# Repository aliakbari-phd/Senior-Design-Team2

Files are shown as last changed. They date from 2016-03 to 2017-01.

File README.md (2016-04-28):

# Wearable Computers for Quantification of Lower Back Disorders
## Team 7: Ben Johnston, Kevin Burns, Alex Dubois, Benny Chan

## Abstract:

Using a combination of wearable inertial sensors and a Microsoft Kinect, our group will create a cost effective system to model the motion of a patient’s lower back in order to quantify the severity of lumbar spinal disorders. This will provide an objective pre-surgical screening, where current methods are largely subjective.

Two small wearable inertial sensors will be placed in line with the patient’s T12 and L5 vertebrae to model integral points on the patient’s back. The patient will be asked to perform simple back exercises to thoroughly evaluate the range of lumbar motion in all planes. The Kinect, a relatively inexpensive motion capturing camera, will be introduced to monitor the patient’s posture and assist the wearable sensors with an all-encompassing look at the subject.

This system would be used in a physician’s clinic room and relatively simple to set up. There are other, more accurate, motion capture systems available that use infrared emission and detection to isolate specific markers on a subject. However, these options consume a large amount of space and cost hundreds of thousands of dollars or more.

## Introduction:

Lower back disorders (LBDs) are the most common work-related musculoskeletal disorders. This translates to a significant cost to society. However, in 80 to 90 percent of cases, precise diagnosis is not known for disabling LBDs. An objective, quantified measure of the severity of lower back disorders is needed. A proven metric can provide a benchmark for returning to the job without risk of exacerbating the disorder, as well as a delineation between normal variability of pain and a disorder.

Our goal is to create a system that can monitor the movement of the patient’s lower back during a specified exercise to characterize and quantify the severity of a lower back disorder. The exercise requires the patient to stand up straight with their arms crossed over one another with their hands resting on their chest. The patient then bends straight down, with their hands remaining on their chest, and returns to the original position. This exercise is repeated as many times as the patient can without undue pain in a 15 second window. This exercise is repeated at 15 degrees, 30 degrees, and as far as the patient can rotate in either direction from the sagittal plane. Repeated motion testing has varied results and can thus be used to provide a full characterization of a human process. 

Our team will combine the use of wearable inertial sensors and a Microsoft Kinect working in tandem to track this motion. The inertial sensors will deliver the pertinent angular characterization of the lower back, and the Kinect will assist in error correction of the inertial sensors as well as ensure proper patient posture throughout the exercise. This data will be synchronized and corrected for standard sensor error. The corrected data will be analyzed to provide the severity quantification as well as being stored on a database. The motion and quantified information will be shown on a graphical user interface on the operator’s computer and posture correction feedback will be shown on a separate display monitor.

## Block Diagram:

Block Diagram

## Concept Sketch:

Concept Sketch

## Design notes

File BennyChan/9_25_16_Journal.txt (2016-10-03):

1. Fixed calculation of flex angle to reflect joint between spineMid and spineBase instead of spineShoulder.
Justification: This is because the location of one of the IMU is located right below the chest, which the SpineMid is closer to compared with the SpineShoulder.
2. Cleaned IMU data from the kinect integration
Justification: The IMU showed unecessary amount of noise, which a low-pass filter of 1K was applied

Tasks:
Test the database of gesture detector to provide more reliable feedback 
Modify GUI as required for patient ease

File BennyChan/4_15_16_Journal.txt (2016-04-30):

Updated Integrated Sensor Code to start implementing data structures

Tasks:
Finish updating integrated sensor code
Create a basic database
Create a basic GUI

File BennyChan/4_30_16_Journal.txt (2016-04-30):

Fixed sagittal angle, computed flex angle and modified GUI to include feedback for angles.

Tasks:
Provide in-depth flowchart
Modify GUI as required

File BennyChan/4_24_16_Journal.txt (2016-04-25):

Created Display Feedback Database, as well as, the GUI for the patient displaying a set of gestures that patient has to do during test.

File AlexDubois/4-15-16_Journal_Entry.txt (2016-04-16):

Updated Integrated Sensor Code to start implementing data structures

Tasks:
Finish updating integrated sensor code
Create a basic database
Create a basic GUI
Find out how to do basic data analysis to find quantified level of LBD

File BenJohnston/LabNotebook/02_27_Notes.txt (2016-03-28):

Sensors are finally online and linked to the computer through Bluetooth with some fancy C# code.

Attended the Design Blitz from 10AM to noon.

Obtained more information on the MotionNet sensor. The actual sensor module is a MPU9150. Datasheet: https://dlnmh9ip6v2uc.cloudfront.net/datasheets/Sensors/IMU/PS-MPU-9150A.pdf

The bluetooth module of the MotionNet Sensor is the BC127, which is bluetooth 4.0. Datasheet: https://developer.mbed.org/media/uploads/bckln/datasheet-bc127.pdf

The batteries used are 400 mAh, 3.7 small batteries. One of them has already died, further reinforcing the aim to rework the power system of the sensors a bit.

I made good progress on the ICD Document. I created the outline and finished my sections of the outline. I redid the formatting of the document template and started to work on my sections.

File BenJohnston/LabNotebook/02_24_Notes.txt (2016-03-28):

We have collected the MotionNet Sensors, a combination of accelerometers, gyroscopes, and magnetometers connected to a bluetooth output on a small PCB, made at UTDallas by Lu Sun Zhongjun, February 2015. We obtained 3 from Jian Wu and a mini-USB cord to hook up the computer.

Jian recommends Visual Studio, as the code for the sensors is written in C#, a graphical version of C. Jian is also sending instructions on how to set them up, some basics physics of how they work, and some other useful info.

These will be the focus of my part of the project, specifically combatting the drift they create.

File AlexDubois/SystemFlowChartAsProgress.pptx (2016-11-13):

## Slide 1

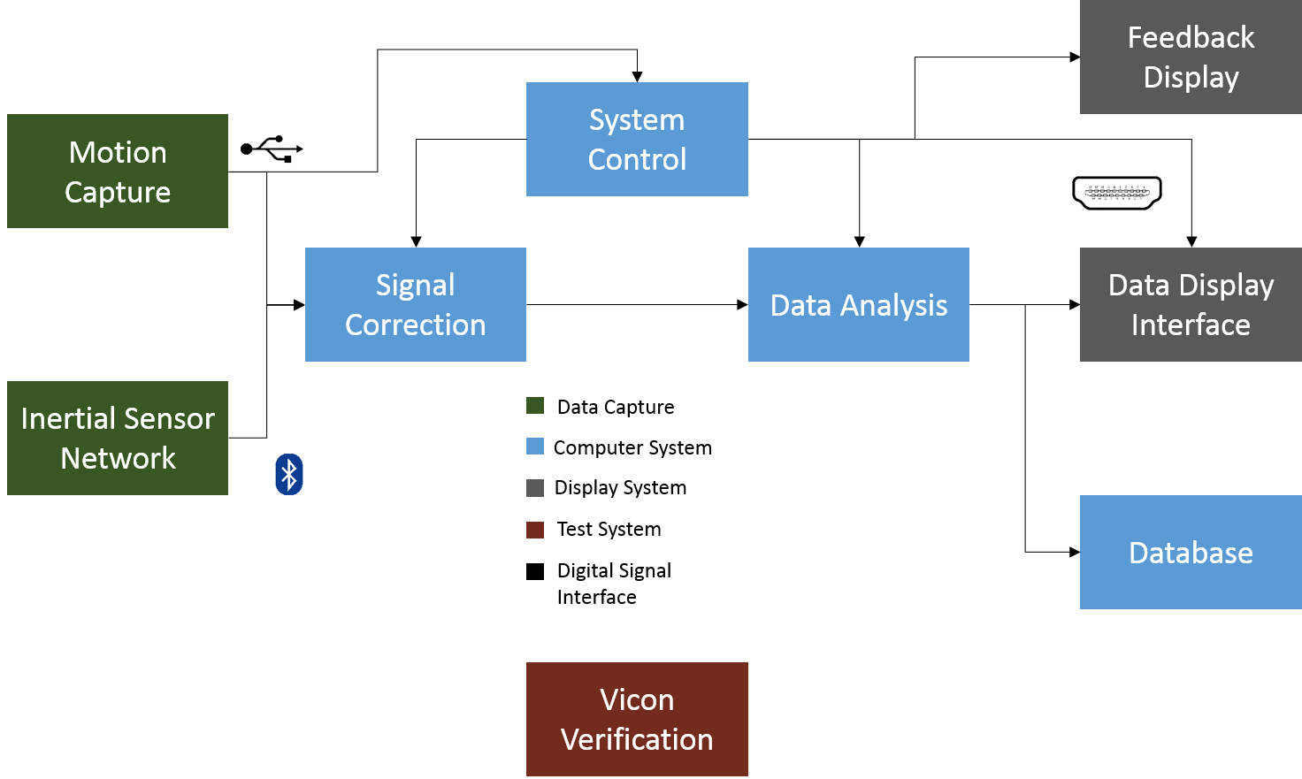
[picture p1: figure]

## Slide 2

Feedback Display

System Control

Motion Capture

Data Display Interface

Inertial Sensor Network

Integrated

Signal Correction

Data Analysis

Database

Requires integration refinement

Not yet integrated

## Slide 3

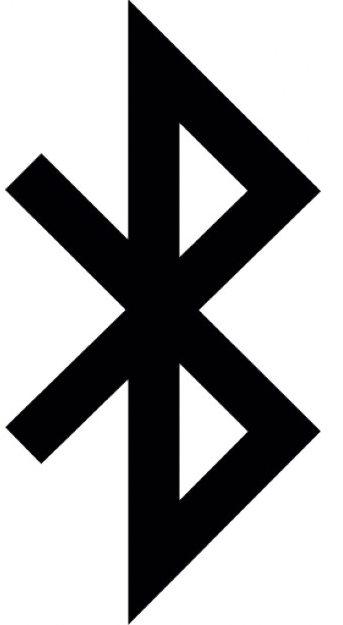
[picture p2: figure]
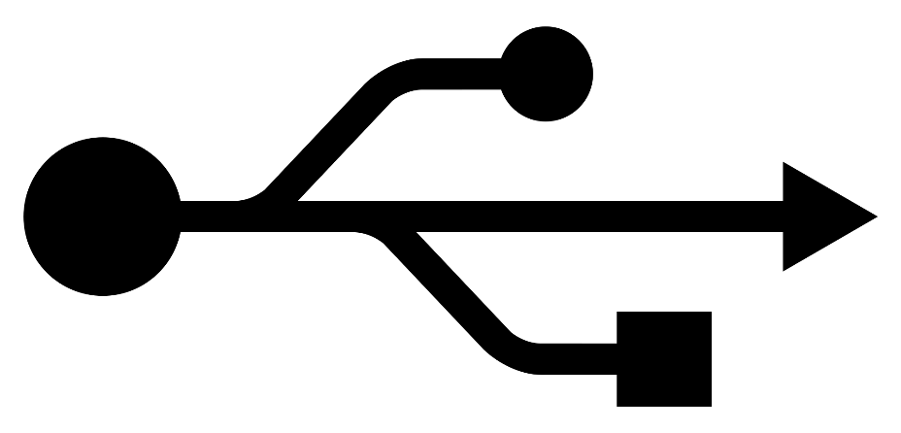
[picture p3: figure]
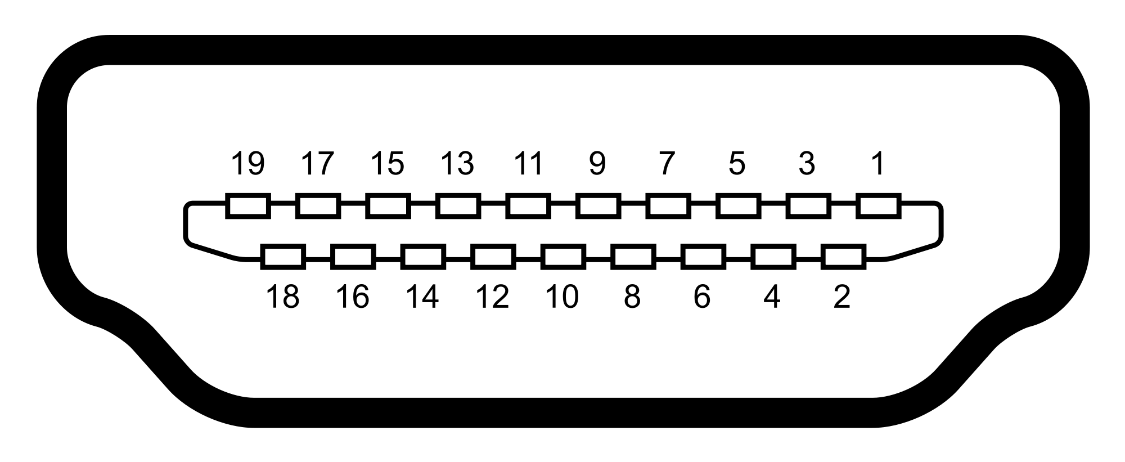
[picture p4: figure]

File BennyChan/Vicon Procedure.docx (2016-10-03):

- Data management to create database
- Select all vicon cameras
  - Window
    - Camera mode
  - If camera doesn’t come up
    - Right click and reboot
- Mask cameras (takes empty points and ignore them)
  - Click mask
  - Whenever they get blue, stop mask
- Aim camera start
- Calibrate
  - Get wand and place it in the origin
  - Calibration, full calibration
  - Selected cameras
  - 2000
  - 750
  - Auto stop check
  - Press start and move wand to calibrate
  - It will auto stop
  - <0.3 is good in image, <0.1 is better
  - Set wand in origin again
- Set volume origin
  - Press start and set origin
- System tab
  - Core processor
    - Reconstruct
- Subject tab
  - Click 2nd icon
    - Click on ben subject model
- Tools tab and go to the little person and select ben.
  - Start subject capture
  - Pipeline
    - Reconstruct
      - Label
        - Esc
    - File I/O
      - Export ascii delimited
- Save and go live

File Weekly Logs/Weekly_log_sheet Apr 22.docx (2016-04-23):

DATE: Apr 22 2016

INDIVIDUAL PROGRESS

Member Name | Accomplishments | Next Week’s Goal | TA Comments
Kevin Burns | C# Sync code completed C# Signal Correction framework finished C# libraries installed and operational | Complete Signal Correction math operations Operational 3D moving line program completed
Benny Chan | Gesture database generated for feedback display Calculation of angle with respect to Kinect GUI for feedback display | Finish gesture database Analyze angle of Kinect
Alex Dubois | Assisted with: Gesture database Kinect Angle | Database for patient information
Ben Johnston | Quaternian forms of signals achieved correctly Swing testing determined variable velocity drift STEP files for enclosure obtained | Use Quaternian form for manipulation Further swing testing performed for long-term drift Build enclosure in SolidWorks

DATE: Apr 22 2016

PROJECT STATUS SUMMARY

MAIN ACCOMPLISHMENTS

- Method for establishing frame from wearable sensors found
- Quaternian representation of signals achieved
- Gestures for pass/fail of exercises with Kinect Gesture Builder built

MAIN PROBLEMS/ISSUES

- Syncing sensor frame with Kinect frame
- What to do with Quaternian representation of signals
- Kinect tracking during rotated trunk exercises

TEAM DYNAMICS

Answer Y or N to each question

- Are all members on schedule with their respective tasks? Yes_
- Are all members contributing equally to the efforts of the team? _Yes_
- If any member is behind schedule, has this occurred consecutively more than one week? _No_
- Would you like to schedule a meeting with any of the TAs to address issues related to team dynamics? _No_

Weekly Log Sheet

ECEN 403 LAB TEAM: 07

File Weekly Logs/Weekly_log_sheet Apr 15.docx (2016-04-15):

DATE: Apr 15 2016

INDIVIDUAL PROGRESS

Member Name | Accomplishments | Next Week’s Goal | TA Comments
Kevin Burns | C# libraries for graphical interface researched C# libraries for mathematical operations downloaded C# software outline completed Proposal completion | Integrate all downloaded libraries to C# Build framework for visualization portion Finish C# program for Synchronization Metronome sensor testing
Benny Chan | Computation of 3d Join position overtime Proposal completion | Resolve frame difference issue between Vicon and Kinect Gesture control
Alex Dubois | Database datastructure framework initialized Quantification measurements researched Proposal completion | Gesture control Finalize quantification measures
Ben Johnston | Altium license accessed and installed and explored Quaternian conversion of motion data Metronome ordered for sensor testing Proposal completion | 3D printed case file exported from Altium Establish frame to work Kinect Metronome sensor testing

DATE: Apr 15 2016

PROJECT STATUS SUMMARY

MAIN ACCOMPLISHMENTS

- Vicon working and data extracted for comparisons to sensors and Kinect for characterization
- Kinect and sensor integrated code for data collection over time
- Shell codes signal processing and data analysis completed

MAIN PROBLEMS/ISSUES

- Reference framing between Kinect and Vicon, as well as well as sensors and Kinect
- Quantification measures need to be researched more and finalized
- More C# code completion

TEAM DYNAMICS

Answer Y or N to each question

- Are all members on schedule with their respective tasks? Yes_
- Are all members contributing equally to the efforts of the team? _Yes_
- If any member is behind schedule, has this occurred consecutively more than one week? _No_
- Would you like to schedule a meeting with any of the TAs to address issues related to team dynamics? _No_

Weekly Log Sheet

ECEN 403 LAB TEAM: 07

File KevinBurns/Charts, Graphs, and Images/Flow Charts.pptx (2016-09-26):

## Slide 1

System Control Subsystem

System Startup Error Handling

IMU Error Handling

Kinect Error Handling

Control Instructions

Feedback Display Instructions

Data Handling Instructions

If: No error

Display No Error

If: Posture Failure

Display Error to Tech

No “Fail”
Flag Detected

“Fail” Flag
Detected

If: System Error

Display Error to Tech

Pass Data to Quantification

Delete Data and Restart Trial

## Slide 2

Signal Syncing Subsystem

Access Sensor Data

Correct Signal Timing Discrepancies

Sensor Data Bank

In MATLAB, needs to convert to C#

No

All Discrepancies Corrected?

Convert Kinect Data from Position to Angular Velocity

Signal Sync Algorithm

Apply Sync Factor and Store Data

Yes

In C#, ready for integration

Drift Correction

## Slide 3

Drift Correction Subsystem

Access Synced IMU Sensor 1 Data

Signal Syncing

Drift Correction Factor

Access Calibration Data

Drift Correction Algorithm

Determine Drift Factor

Repeat for IMU Sensor 2

Apply Drift Correction to Data

Store Data for Use in Quantification

Quantification

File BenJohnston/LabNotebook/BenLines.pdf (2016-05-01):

- Intro(4+4+4+7+6+4)=29 seconds
- We’re Team 7, Wearable Computers for the Quantification of Lower Back Disorders
- We are mentored by Dr. Jafari of ESP Lab at Texas A&M University
- We’re using wearable inertial sensors combined with a Microsoft Kinect to gather data to model a patient’slower back, and then transmit that data to a central computer.
- These signalswill be synchronized, corrected, and analyzed, giving a quantification of the severity of the patient’s lower back disorder.
- This information will be stored in a database and displayed for a medical technician.
- Wearables(7+6+8+7+6+7)=41 seconds
- Two MotionNet sensors, provided by ESP Lab, will be placed along the lumbar region of the patient’s spine, secured and buttoned to Polar Soft Straps.
- I have collected over 20 hours of tests from the sensors in an attempt to characterize the “drift” error of the IMU’s gyroscopes.
- “Drift” error compounds, reducing the accuracy of the sensors over a long period of time as seen from the raw data on the left. On the right is the correction I have developed thus far.
- Current drift correction models are not viable for hour plus long intervals. Which is the goal for repeated testing without recharging the sensors.
- I will use the accelerometers and Kinect to error check and further the accuracy of the gyroscopes through Kalman filters.
- Additionally, there is a small amount of movement between the PCB and the existing 3D box case, so I am working to print a new, fitted enclosure.
- Vicon (8+5+8)=21 seconds
- We will use a Vicon, a highly accurate motion capture system of infrared cameras focused on a central point, to verify the accuracy of the IMU’s and Kinect.
- Ben Johnston is seen here demonstrating the trunk flex exercise, along with the resultant camera view of the Vicon.
- TheIMU’s, Kinect, and Vicon data must be interpolated into the same relative global frame for the verification. This will be accomplished in the coming months.

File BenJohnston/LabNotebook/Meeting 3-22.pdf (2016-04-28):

# Sensor Presentation

3/22

15 seconds, velocity and best fit line

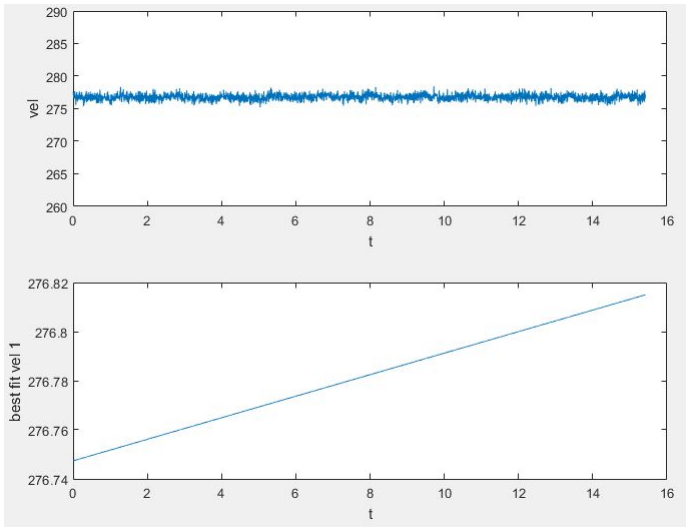
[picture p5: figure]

30 seconds velocity and best fit line

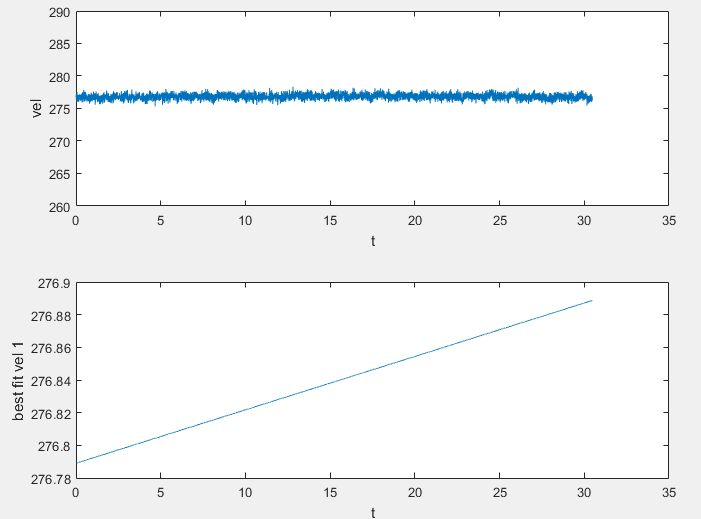
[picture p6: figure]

60 seconds velocity and best fit line

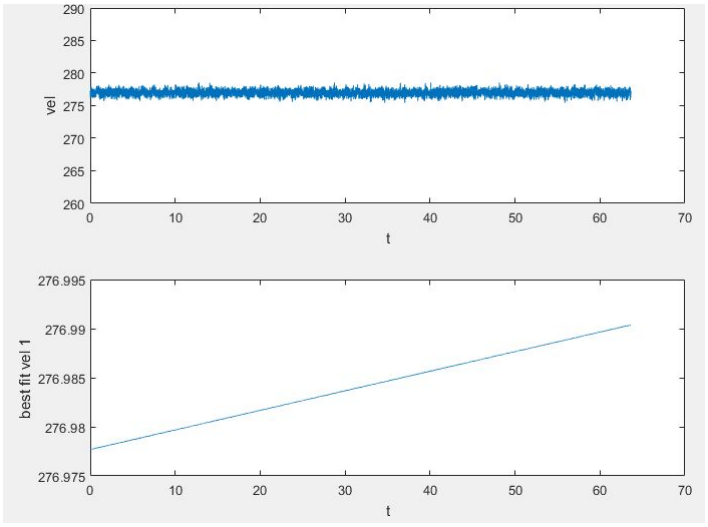
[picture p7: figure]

5 min velocity and best fit line

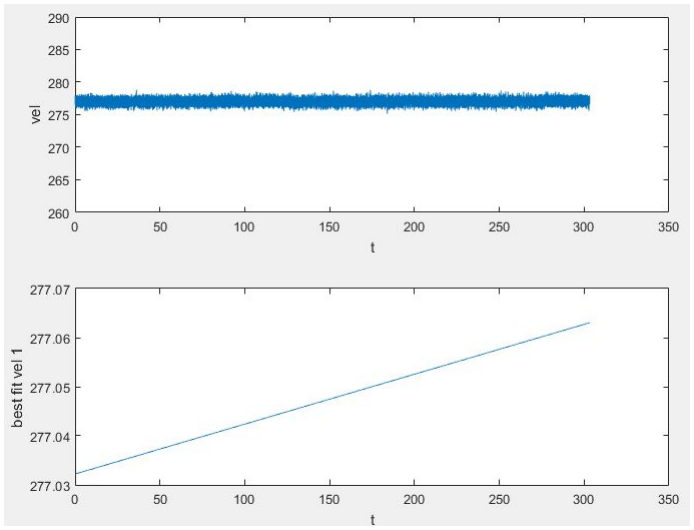
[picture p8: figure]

15 sec, 30 sec, 1 min, 5 min velocities over time

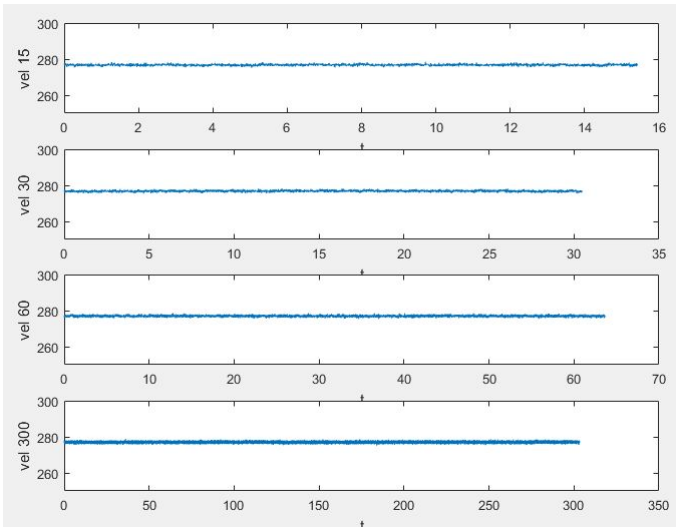
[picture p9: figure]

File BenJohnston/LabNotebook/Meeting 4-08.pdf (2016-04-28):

# Wearable Sensor Testing Report 4/8/2016

All of the following results are from older data with the wearables configured to capture at 200 Hz. When the sensors were changed to 500 Hz, the actual capture rate was inconsistent and the data suffered as a result and was thus unusable. This is what I was trying to convey in an admittedly confusing manner before. I've run many tests but I will highlight a few that I believe to be important. All of the following tests were using the same sensor. Results vary slightly with the sensor, but I wished the following data to be consistent.
Note: All following velocities and distances are found in the Z-axis of the gyroscope.

## LP Player Test

- The following test involves an inertial sensor placed on a rotating LP player.
- Player rotating at 45 rpm (270 degrees per second).
- Test run for 63.02 seconds

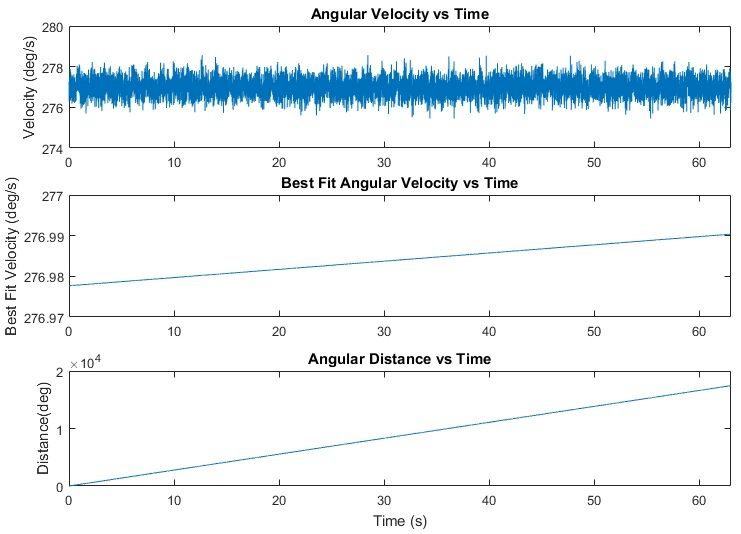
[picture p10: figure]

- Mean Velocity: 276.98 | deg/s | Expected: 270 deg/s
- Final Distance: 17455 deg | | Expected: 17014.4 deg
It is difficult to know how much of the discrepancy between actual and expected is due to inaccuracy in the “45 rpm” setting of the LP player and due to the drift.

## Stationary Test (Power Unplugged vs Plugged)

- Test consists of sensor sitting stationary on undisturbed surface.
- Test run for 7199.2 sec (~2 hours).
- Sensor fully charged and then unplugged.

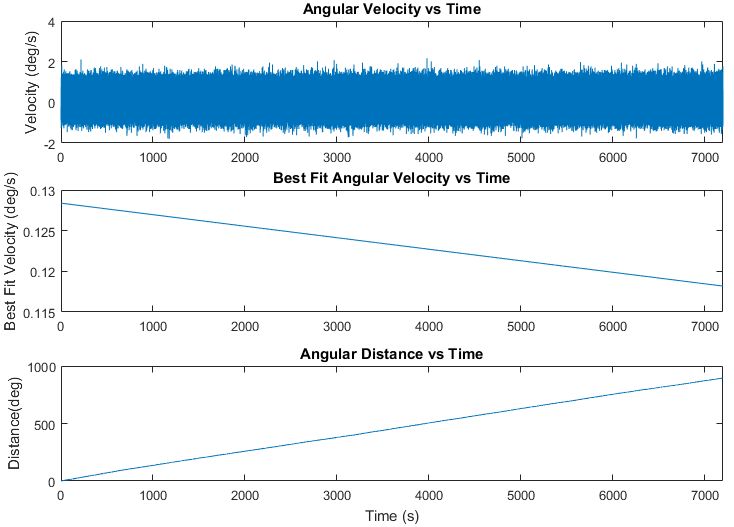
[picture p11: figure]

- Mean Velocity: | 0.123 deg/s | Expected: 0
- Final Distance: | 895.14 deg | Expected: 0
- Corrected Distance: 858.44 deg
- Drift: | 0.0102 deg
“Drift” refers to the difference in starting velocity from the best linear fit line and the ending best fit ending velocity.
Velocity is corrected by subtracting the discrepancy in initial best fit velocity from current best fit velocity from it. Or more simply put, flattening out the best fit line and adjust velocity by the
same amount.
This correction fixes the data by only 4.2%. I believe the main problem to be the inherent offset that the gyroscopes are reading. Even when noise is filtered with a digital low pass filter, there is a clear average offset of ~0.13 degrees per second. This number is different for each sensor. Drift is certainly a function of the voltage of the battery, as shown in the test below with the power cord plugged in for the duration.

- Test is run with sensor sitting stationary on undisturbed surface.
- Sensor fully charged, and plugged into power cord for the duration of test.
- Test run for 7197.9 sec (~2 hours)

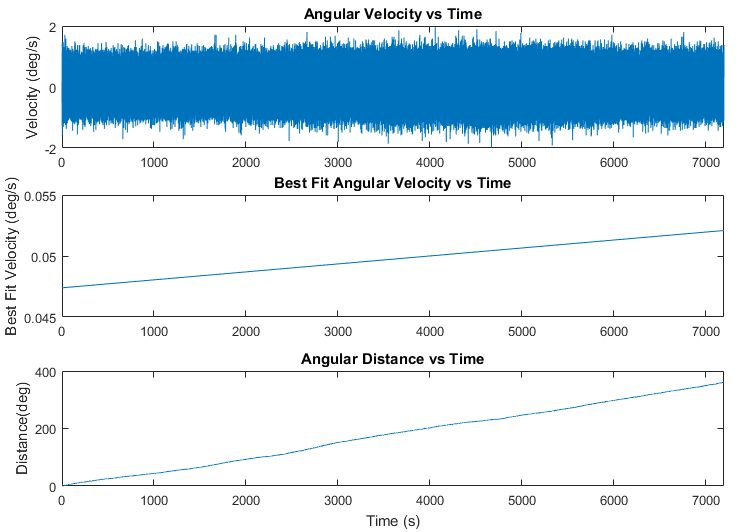
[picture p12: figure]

- Mean Velocity: | 0.0497 deg/s | Expected: 0
- Distance: | 360.75 deg | Expected: 0
- Corrected Distance: 343.84 deg
- Drift: | 0.0047 deg
These results are nearly 2.5 times better than where a sensor is not plugged in. I believe that it would be worth looking into a battery that would more consistently deliver voltage for a longer period of time. This must be taken into account when 3D printing an enclosure for the sensor.

Thank you for your time Dr. Jafari. Please let me know if you have any further questions about my results thus far.

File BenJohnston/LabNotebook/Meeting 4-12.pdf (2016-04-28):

# Inertial Wearable Sensors Presentation

4/12/2016

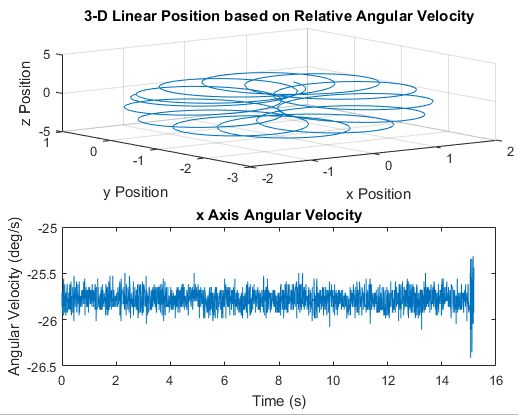
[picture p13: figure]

Test Parameters
- Sensor placed on rotating LP player (rotates in z-axis).
- Duration: 15.18 s
- Capture Rate: 203.1 Hz

Results:
- Actual Z Distance: 4203 deg
- Expected Distance: 4099 deg
- Actual Z Velocity: 277 deg/s
- Expected Velocity: 270 deg/s

Raw Data
- Linear position found based on relative angular velocity.
- Position units are multiplied by radius to find actual position.

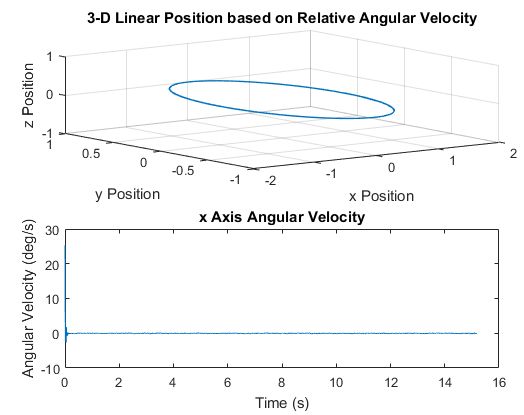
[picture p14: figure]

With Correction

- Angular velocity low pass filtered for noise
- Average velocity recorded while sensor stationary,
treated as constant offset
- Offset subtracted velocity recorded in motion

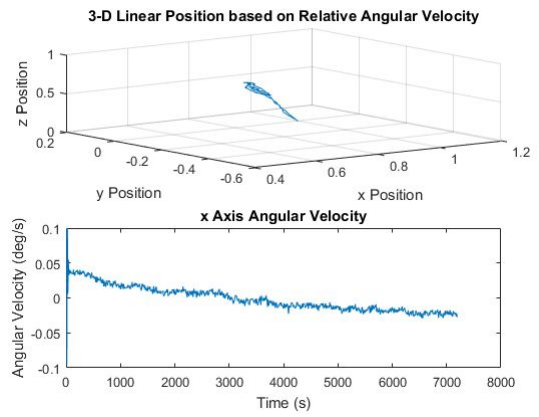
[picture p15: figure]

Test Parameters:
- Sensor stationary on
undisturbed surface.
- Duration: 7199.2 sec (~2hr)
- Capture Rate: 203.0 Hz

Results:
- Voltage Drift (Defined as the difference in starting
angular velocity subtracted by end angular velocity):
0.0597 degrees
- Slope of Drift:
8.293*10^-6 deg/s

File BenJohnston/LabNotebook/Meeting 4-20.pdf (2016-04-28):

# Inertial Sensor Presentation

4/20

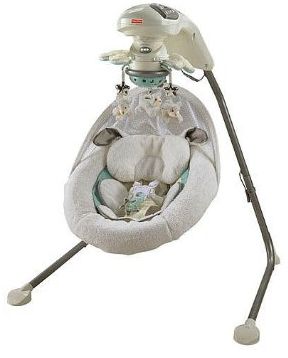
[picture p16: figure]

Fisher Price Platinum Edition Cradle n’ Swing

- Metronome alternative.
- Only suitable metronome: expensive and 3 weeks to ship
- Not perfectly stable in off axes
- Takes time to speed up
- Exact speeds, measurements not known
- Test: Is the ending position same as starting position?

Stationary Testing for Offset Velocity

- Sensor: 01623D
- Test: sensor placed on undisturbed surface for 60 seconds.

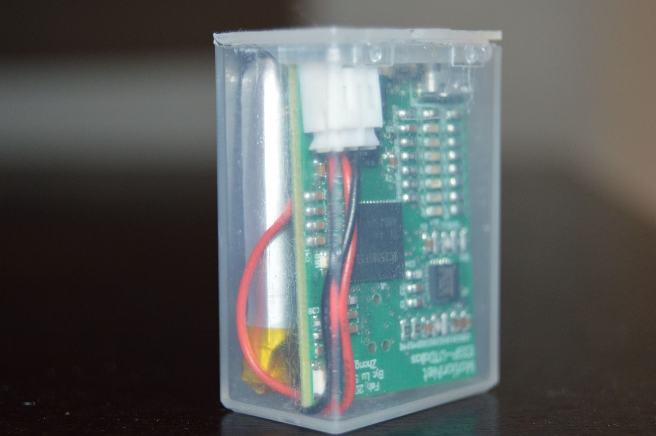
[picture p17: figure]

- Velocity is low pass filtered for noise
- Average velocities in x,y,z are treated as constant offsets
- Mean_x: | -1.2012 deg/s
- Mean_y: | -0.7176 deg/s
- Mean_z: | 0.8495 deg/s

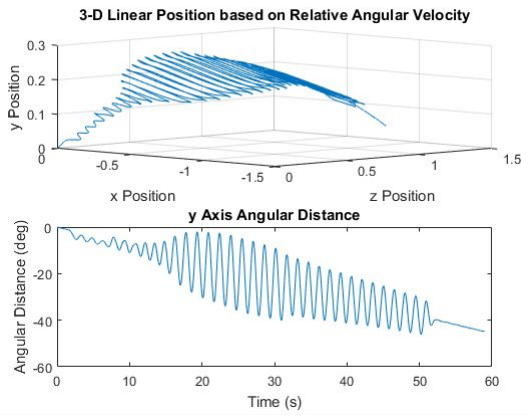
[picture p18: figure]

Results (without correction)

- Sensor taped to seat of
swing, swing powered on
- 15 seconds until desired speed achieved (level 4/6)
- 15 seconds run time at
desired speed
- 20 seconds slowing down
after power off
- Stopped by hand at 52
second mark

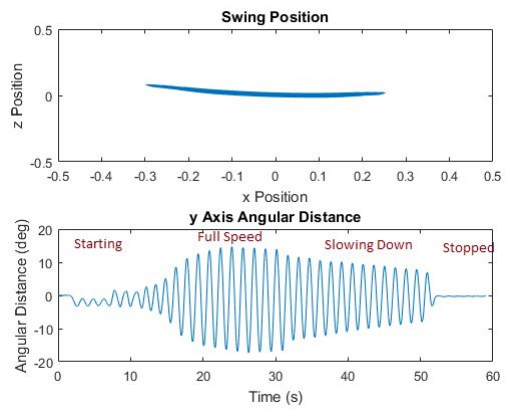
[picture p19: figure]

Results (Drift Corrected)

- Offset velocities from
stationary test
subtracted from swing
test.
- Swing motion is now
apparent.
- Most importantly,
Y position starts at zero, and ends at zero with
correction.

## Where to go from here?

- Work with Kevin’s calibration to ensure that one initial calibration reliably reports offset velocity for an extended period of time
- Enclosure for sensors with Altium .STEP files. Need to discuss new harness design ideas (one wide compression belt)
- Further work converting to quaternion format, using accelerometers and Kinect to enhance gyroscope accuracy

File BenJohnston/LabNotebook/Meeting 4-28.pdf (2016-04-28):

# Inertial Wearable Sensors

4/28

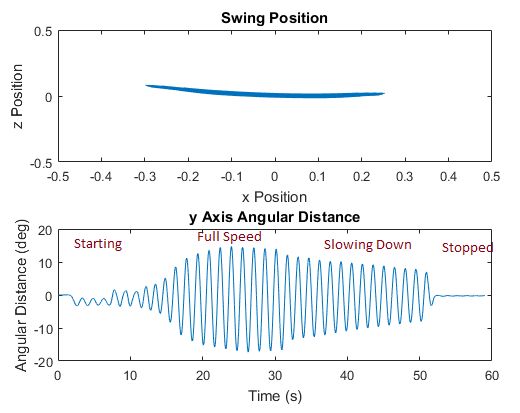
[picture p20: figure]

2 Hour Swing Test

- Fisher Price Platinum
Edition Cradle n’ Swing
- Powered on run at 4/6
speed for 2 hours.
- Powered off, stopped
by hand.

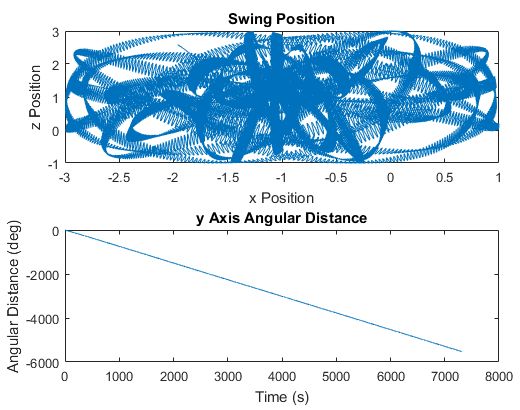
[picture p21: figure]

Uncorrected Data

- Clear Drift
- ~5500 degrees from
start after 2 hours

Corrected Data:

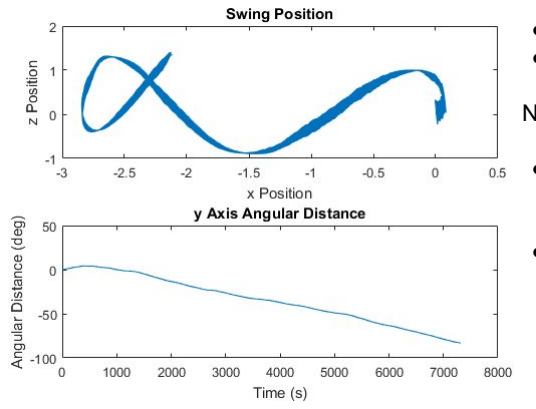
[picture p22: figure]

- Offset correction method used
- Not viable for 2 hours

Next Steps:

- Further testing to establish at what line offset correction is no longer viable
- IMU sensor fusion

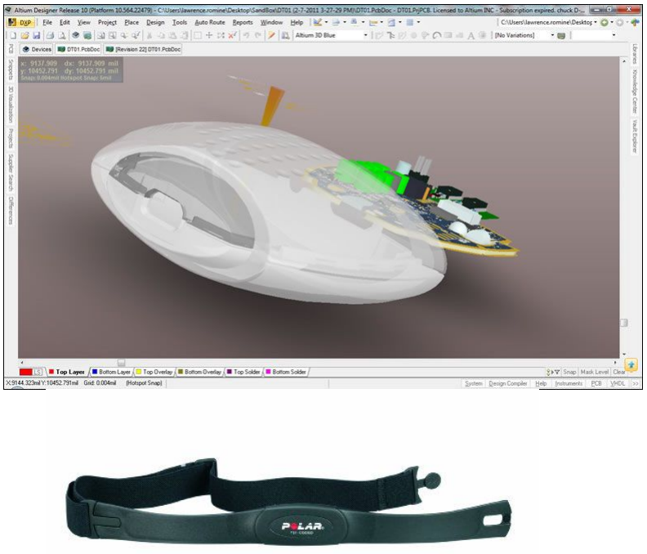
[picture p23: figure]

Other Focuses:

- PCB Enclosure
- Polar Heart Rate Monitor Strap for securing
sensors?
- Further interpolation work

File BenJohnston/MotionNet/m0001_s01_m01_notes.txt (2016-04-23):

row	name		port	note
1	RemoteXXXX	12	

General Notes
DEBUG-> INITIALIZING ALL CHECKED NODES
DEBUG->    begin init[0] node 1 : RemoteXXXX : COM12
DEBUG->    begin init[1] node 2 : RemoteXXXX : COM14
DEBUG-> SUCCESS INITIALIZING ALL CHECKED NODES
DEBUG->       Opened COM12
DEBUG->       Opened DCB12
DEBUG->       Opened COM14
DEBUG->       Opened DCB14
DEBUG-> READING FROM ALL CHECKED NODES
DEBUG-> SUCCESS READING ALL CHECKED NODES
DEBUG-> CLOSING ALL CHECKED NODES
DEBUG->    begin close[0] node 1 : RemoteXXXX : COM12
DEBUG->       Closed COM12
DEBUG->       Closed File D:/Ben TAMU/MotionNet/Executable/Split/m0001_s01_m01_n01.txt
DEBUG->    Success close[0] node 1 : RemoteXXXX : COM12
DEBUG->    begin close[1] node 2 : RemoteXXXX : COM14
DEBUG->       Closed COM14
DEBUG->       Closed File D:/Ben TAMU/MotionNet/Executable/Split/m0001_s01_m01_n02.txt
DEBUG->    Success close[1] node 2 : RemoteXXXX : COM14
DEBUG-> SUCCESS CLOSING ALL CHECKED NODES
DEBUG->       Closed File C:/Users/Chasareth_2/Documents/GitHub/Team7/BenJohnston/MotionNet/Split/New Sensor/m0001_s01_m01_notes.txt
DEBUG-> INITIALIZING ALL CHECKED NODES
DEBUG->    begin init[0] node 1 : RemoteXXXX : COM12
DEBUG-> SUCCESS INITIALIZING ALL CHECKED NODES
DEBUG->       Opened COM12
DEBUG->       Opened DCB12
DEBUG-> READING FROM ALL CHECKED NODES
DEBUG-> SUCCESS READING ALL CHECKED NODES
DEBUG-> CLOSING ALL CHECKED NODES
DEBUG->    begin close[0] node 1 : RemoteXXXX : COM12
DEBUG->       Closed COM12
DEBUG->       Closed File C:/Users/Chasareth_2/Documents/GitHub/Team7/BenJohnston/MotionNet/Split/New Sensor/Split/m0001_s01_m01_n01.txt
DEBUG->    Success close[0] node 1 : RemoteXXXX : COM12
DEBUG-> SUCCESS CLOSING ALL CHECKED NODES
DEBUG->       Closed File C:/Users/Chasareth_2/Documents/GitHub/Team7/BenJohnston/MotionNet/Split/New Sensor/m0001_s01_m01_notes.txt
DEBUG-> INITIALIZING ALL CHECKED NODES
DEBUG->    begin init[0] node 1 : RemoteXXXX : COM12
DEBUG-> SUCCESS INITIALIZING ALL CHECKED NODES
DEBUG->       Opened COM12
DEBUG->       Opened DCB12
DEBUG-> READING FROM ALL CHECKED NODES
DEBUG-> SUCCESS READING ALL CHECKED NODES
DEBUG-> CLOSING ALL CHECKED NODES
DEBUG->    begin close[0] node 1 : RemoteXXXX : COM12
DEBUG->       Closed COM12
DEBUG->       Closed File C:/Users/Chasareth_2/Documents/GitHub/Team7/BenJohnston/MotionNet/Split/New Sensor/Split/m0001_s01_m01_n01.txt
DEBUG->    Success close[0] node 1 : RemoteXXXX : COM12
DEBUG-> SUCCESS CLOSING ALL CHECKED NODES
DEBUG->       Closed File C:/Users/Chasareth_2/Documents/GitHub/Team7/BenJohnston/MotionNet/Split/New Sensor/m0001_s01_m01_notes.txt
DEBUG-> INITIALIZING ALL CHECKED NODES
DEBUG->    begin init[0] node 2 : RemoteXXXX : COM14
DEBUG-> SUCCESS INITIALIZING ALL CHECKED NODES
DEBUG->       Opened COM14
DEBUG->       Opened DCB14
DEBUG-> READING FROM ALL CHECKED NODES
DEBUG-> SUCCESS READING ALL CHECKED NODES
DEBUG-> CLOSING ALL CHECKED NODES
DEBUG->    begin close[0] node 2 : RemoteXXXX : COM14
DEBUG->       Closed COM14
DEBUG->       Closed File C:/Users/Chasareth_2/Documents/GitHub/Team7/BenJohnston/MotionNet/Split/New Sensor/Split/m0001_s01_m01_n02.txt
DEBUG->    Success close[0] node 2 : RemoteXXXX : COM14
DEBUG-> SUCCESS CLOSING ALL CHECKED NODES
DEBUG->       Closed File C:/Users/Chasareth_2/Documents/GitHub/Team7/BenJohnston/MotionNet/Split/m0001_s01_m01_notes.txt
DEBUG-> INITIALIZING ALL CHECKED NODES
DEBUG->    begin init[0] node 2 : RemoteXXXX : COM14
DEBUG-> SUCCESS INITIALIZING ALL CHECKED NODES
DEBUG->       Opened COM14
DEBUG->       Opened DCB14
DEBUG-> READING FROM ALL CHECKED NODES
DEBUG-> SUCCESS READING ALL CHECKED NODES
DEBUG-> CLOSING ALL CHECKED NODES
DEBUG->    begin close[0] node 2 : RemoteXXXX : COM14
DEBUG->       Closed COM14
DEBUG->       Closed File C:/Users/Chasareth_2/Documents/GitHub/Team7/BenJohnston/MotionNet/Split/Split/m0001_s01_m01_n02.txt
DEBUG->    Success close[0] node 2 : RemoteXXXX : COM14
DEBUG-> SUCCESS CLOSING ALL CHECKED NODES
DEBUG->       Closed File C:/Users/Chasareth_2/Documents/GitHub/Team7/BenJohnston/MotionNet/Split/m0001_s01_m01_notes.txt
DEBUG-> INITIALIZING ALL CHECKED NODES
DEBUG->    begin init[0] node 1 : RemoteXXXX : COM12
DEBUG-> SUCCESS INITIALIZING ALL CHECKED NODES
DEBUG->       Opened COM12
DEBUG->       Opened DCB12
DEBUG-> READING FROM ALL CHECKED NODES
DEBUG-> SUCCESS READING ALL CHECKED NODES
DEBUG-> CLOSING ALL CHECKED NODES
DEBUG->    begin close[0] node 1 : RemoteXXXX : COM12
DEBUG->       Closed COM12
DEBUG->       Closed File C:/Users/Chasareth_2/Documents/GitHub/Team7/BenJohnston/MotionNet/Split/Split/m0001_s01_m01_n01.txt
DEBUG->    Success close[0] node 1 : RemoteXXXX : COM12
DEBUG-> SUCCESS CLOSING ALL CHECKED NODES
DEBUG->       Closed File C:/Users/Chasareth_2/Documents/GitHub/Team7/BenJohnston/MotionNet/m0001_s01_m01_notes.txt
DEBUG-> INITIALIZING ALL CHECKED NODES
DEBUG->    begin init[0] node 1 : RemoteXXXX : COM12
DEBUG-> SUCCESS INITIALIZING ALL CHECKED NODES
DEBUG->       Opened COM12
DEBUG->       Opened DCB12
DEBUG-> READING FROM ALL CHECKED NODES
DEBUG-> SUCCESS READING ALL CHECKED NODES
DEBUG-> CLOSING ALL CHECKED NODES
DEBUG->    begin close[0] node 1 : RemoteXXXX : COM12
DEBUG->       Closed COM12
DEBUG->       Closed File C:/Users/Chasareth_2/Documents/GitHub/Team7/BenJohnston/MotionNet/Split/m0001_s01_m01_n01.txt
DEBUG->    Success close[0] node 1 : RemoteXXXX : COM12
DEBUG-> SUCCESS CLOSING ALL CHECKED NODES

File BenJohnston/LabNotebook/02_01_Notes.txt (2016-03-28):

Our team is:
Ben Johnston – EE (me)
Kevin Burns – EE
Benny Chan – CE
Alex Dubois – CE

We will be working with the Biomedical Engineering department at Texas A&M to create wearable electronics.

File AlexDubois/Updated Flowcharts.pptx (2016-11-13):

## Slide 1

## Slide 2

Completed

In Progress

Not started

Standby

Receive corrected data structure

Start

Analysis

Calculate lists of angle, angular acceleration, and angular jerk

Compare against LBD severity model

Calculate closest level of LBD

Database

Calculate final severity across all trials

Generate Patient ID

Add supporting data and LBD severity to database

End

Output database information to DDI

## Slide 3

Completed

In Progress

Not started

Render Initial View

Standby

Start

Interface

Receive User Input

Process specified function

Data Display

Receive Data Analysis

Display supporting data and LBD severity

Go back to start

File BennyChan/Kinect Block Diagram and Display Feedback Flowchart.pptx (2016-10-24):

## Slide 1

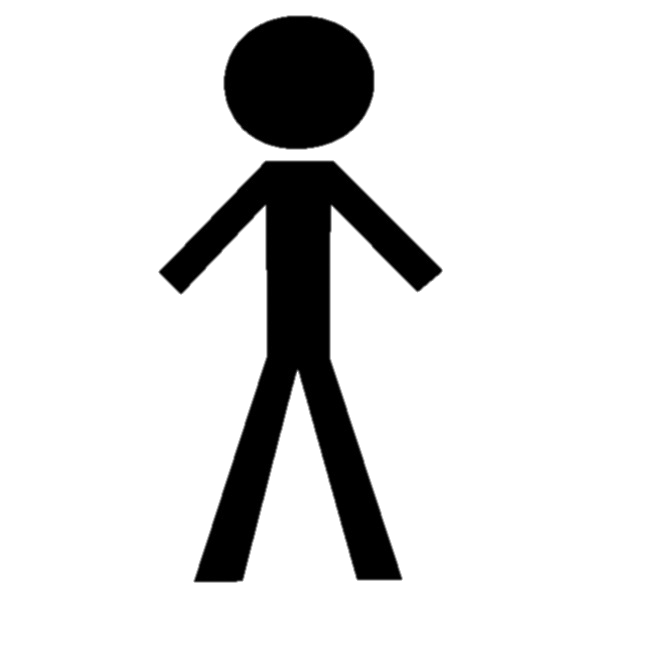
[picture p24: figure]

Obtain joint of interest

3D position

Capture Local Timestamp

Posture estimation

Compute Sagittal and Flex angle


Send to Signal Correction Unit

Completed

Requires Refinement

Vicon

Send to Feedback Display

Not yet Implemented

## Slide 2

Test – Flexion of Body at 30 Degrees


2 – Tracked
1 - Inferred

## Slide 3

Render Initial View

Standby

Tracked Body?

No

Yes

Visual Gesture Builder

Gesture Database

Compute Sagittal & Flex Angle

Error?

Kinect Studio

Recorded Clips

No

Update Message

Completed

Requires Refinement

Parse Error Code

Update Error Message

Not yet Implemented

Go back to standby

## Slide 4


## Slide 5

Posture estimation

Compute Sagittal and Flex angle

Send to Signal Correction Unit

Obtain joint of interest

3D position

Completed

Requires Refinement

Vicon

Not yet Implemented

Send to Feedback Display

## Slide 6

Render Initial View

Standby

Tracked Body?

No

Completed

Requires Refinement

Yes

Not yet Implemented

Gesture Database

Compute Sagittal & Flex Angle

Error?

No

Update Message

Go back to standby

Update Error Message



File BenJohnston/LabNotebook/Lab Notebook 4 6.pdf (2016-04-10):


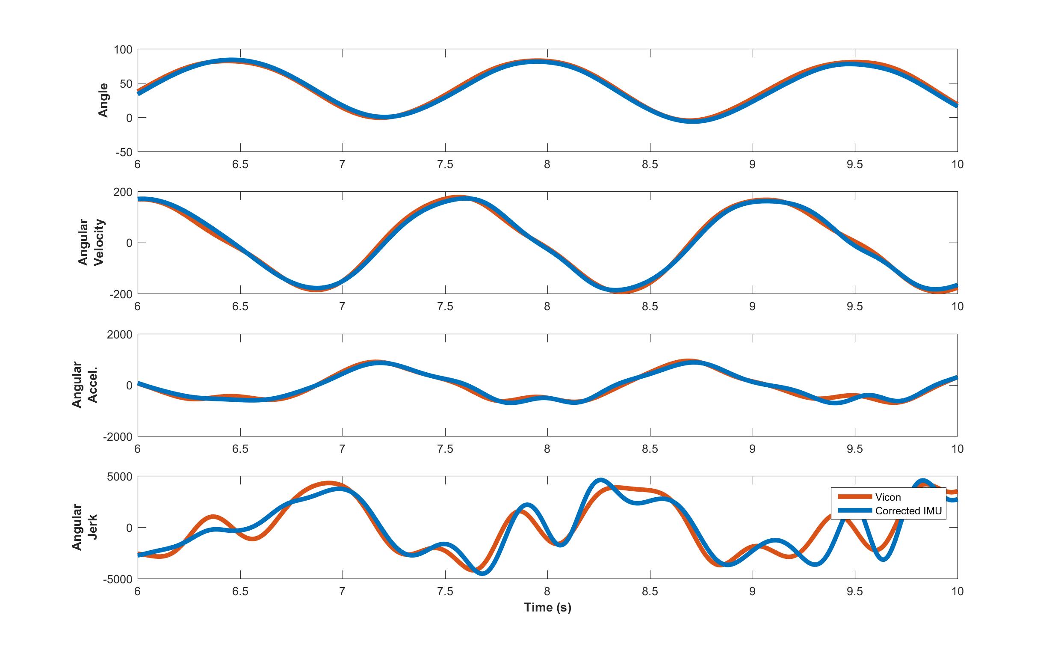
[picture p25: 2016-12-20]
SystemTestReadings/9 - 25/CorrectedPosterPlotv2.jpg

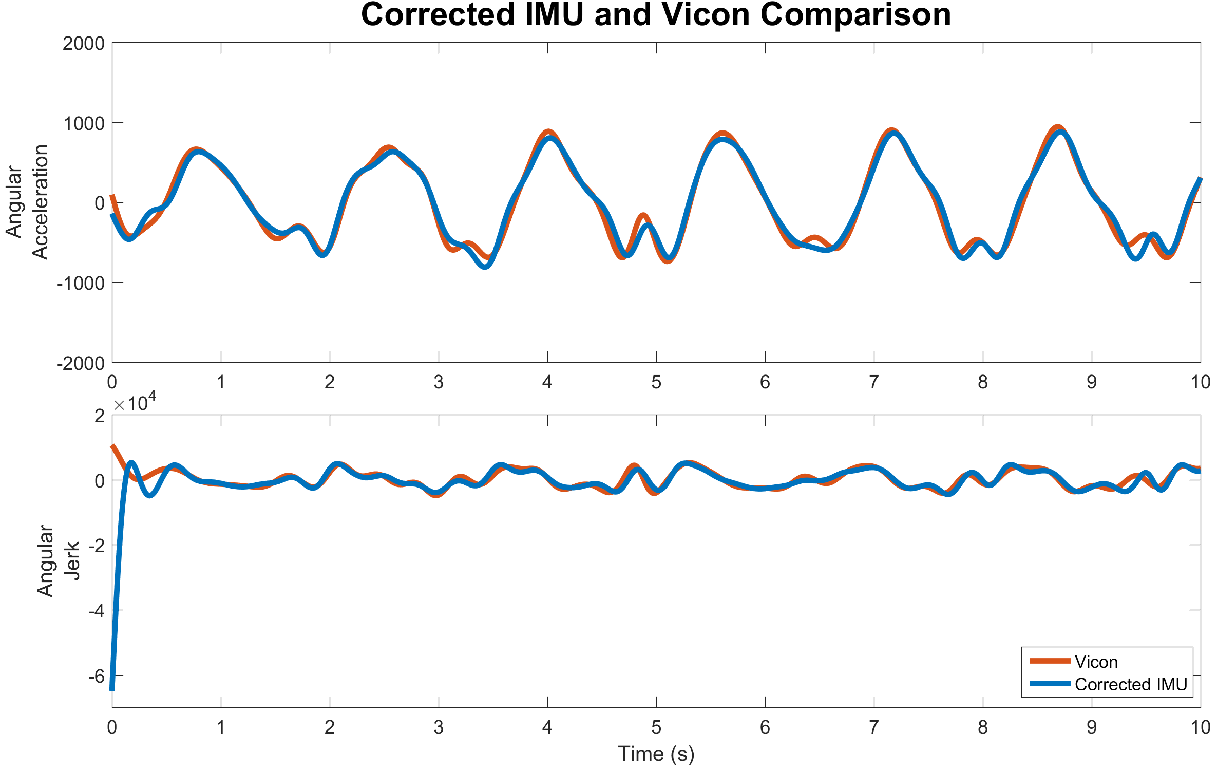
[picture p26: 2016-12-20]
SystemTestReadings/9 - 25/CorrectedPosterPlotv2bot2only.PNG

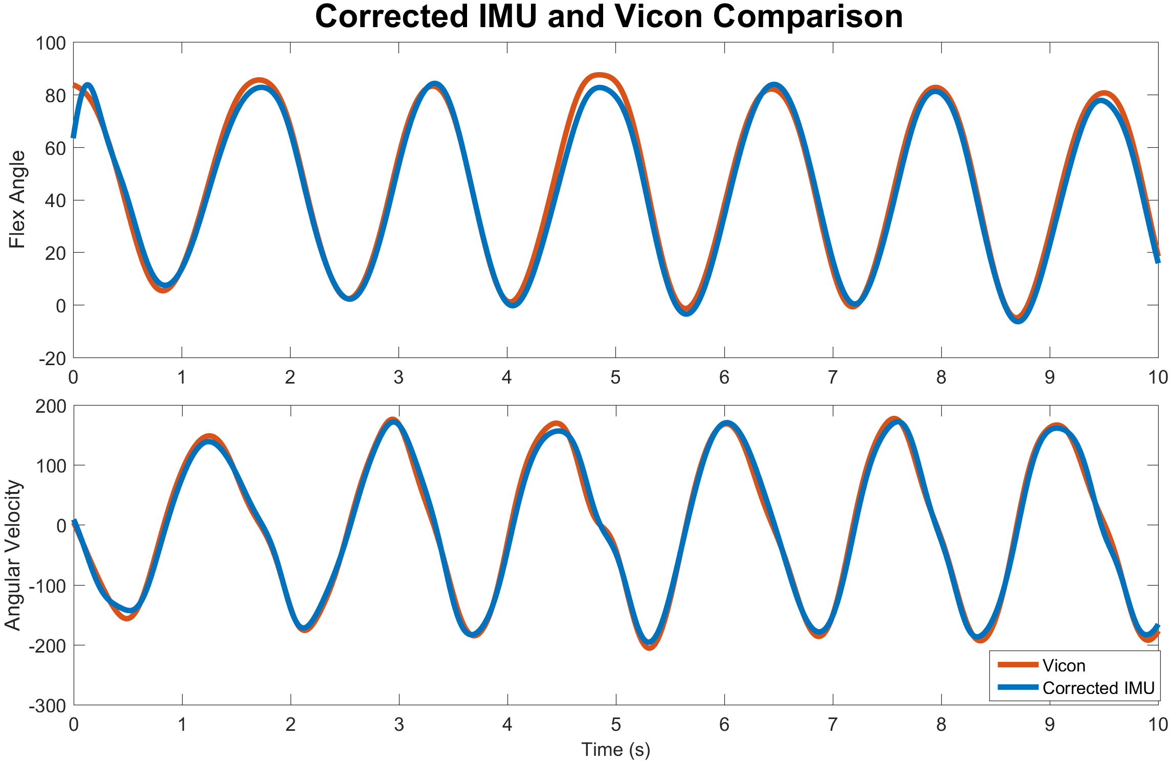
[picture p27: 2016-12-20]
SystemTestReadings/9 - 25/CorrectedPosterPlotv2top2only.PNG

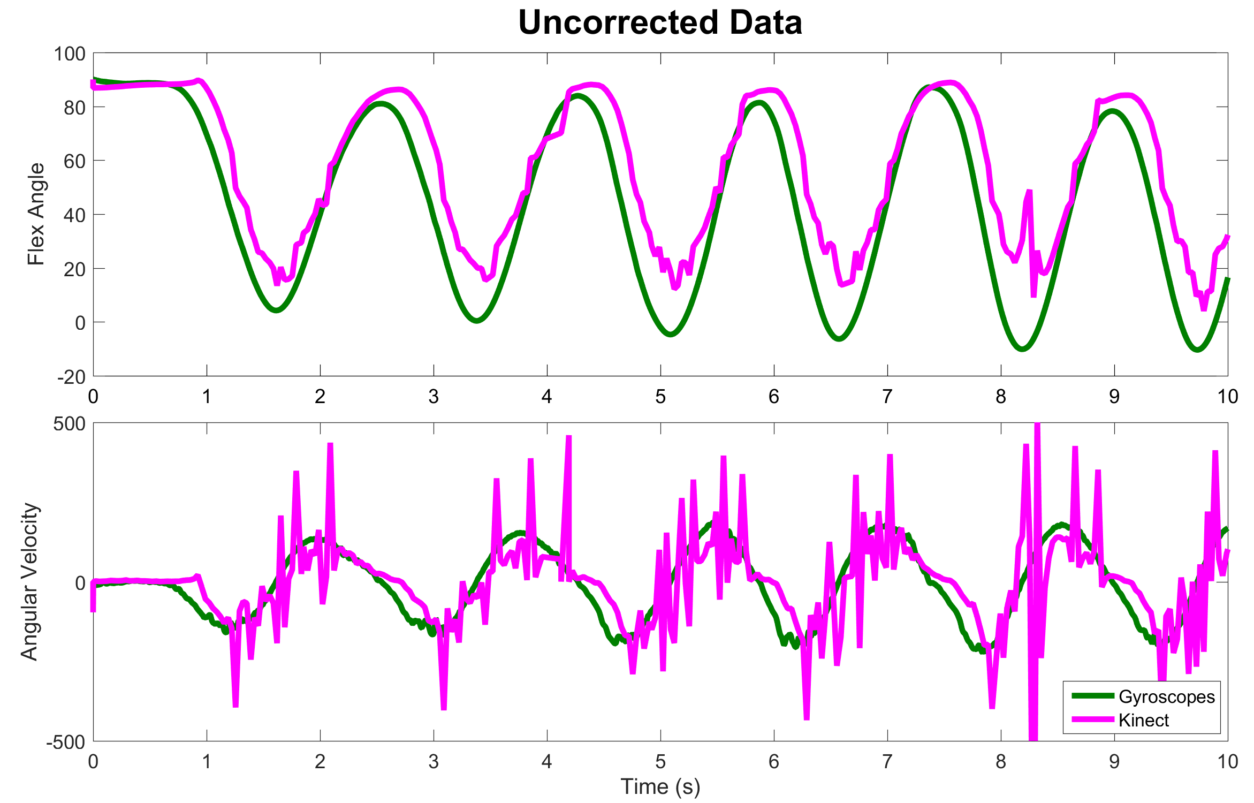
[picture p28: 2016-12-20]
SystemTestReadings/9 - 25/UncorrectedPosterPlotv2top2only.PNG

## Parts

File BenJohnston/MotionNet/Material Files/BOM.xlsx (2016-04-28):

Part Number | Description | Component | Quantity
CC2538 | IC SOC IEEE 802.15.4/ZBEE | U1 | 1 | http://www.digikey.com/product-detail/en/CC2538SF53RTQT/296-35797-1-ND/4030167
BC127 | DUAL MODE BT LE V4.0 MOD W/ANT | U2 | 1 | http://www.digikey.com/product-detail/en/BC127/1495-1000-1-ND/4733175
TPS22901YFPR | IC LOAD SWITCH ULOW RDS 4DSBGA | U3, U7, U9 | 3 | http://www.digikey.com/product-detail/en/TPS22901YFPR/296-24771-1-ND/2092593
BQ24073 | IC LI-ION CHARGE/PWR MGMT 16-QFN | U4 | 1 | http://www.digikey.com/product-detail/en/BQ24073RGTT/296-23839-1-ND/1960945
TPS79133 | IC REG LDO 3.3V 0.1A SOT23-5 | U5 | 1 | http://www.digikey.com/product-detail/en/TPS79133DBVR/296-11866-1-ND/381441
MPU9150A | GYRO/ACCELEROMETER 9-AXIS 24LGA | U6 | 1 | http://www.digikey.com/product-detail/en/MPU-9150/1428-1009-1-ND/4038014
SDCard-3M | CONN EJECT MICROSD PUSH-PUSH SMD | U8 | 1 | http://www.digikey.com/product-detail/en/2908-05WB-MG/3M5607CT-ND/1242498
2450BM15A0002 | BALUN JTI MATCHED ZIGBEE | U10 | 1 | http://www.digikey.com/product-detail/en/2450BM15A0002E/712-1536-1-ND/2392136
2450AT18A100 | ANTENNA CHIP 2.4GHZ | A1 | 1 | http://www.digikey.com/product-detail/en/2450AT18A100E/712-1005-1-ND/1560834
ABS06-32.768KHZ-T | CRYSTAL 32.768KHZ 12.5PF SMD | Y1(32kHz) | 1 | http://www.digikey.com/product-detail/en/ABS06-32.768KHZ-T/535-10104-1-ND/2089921
ABM8X-102-32.000MHz | CRYSTAL 32MHZ 10PF SMD | Y2(32MHz) | 1 | http://www.digikey.com/product-detail/en/ABM8X-102-32.000MHZ-T/535-11454-1-ND/2673402
TC2030-IDC-NL |  | J1(JTAG)
3-175635-6 | CONN HEADER 6POS DUAL 1MM SMD | J3 | 1 | http://www.digikey.com/product-detail/en/FTMH-103-03-L-DV/SAM1131-03-ND/1104450
S2B-PH-K-S(LF)(SN) | CONN HEADER PH SIDE 2POS 2MM | J4(battery) | 1 | http://www.digikey.com/product-search/en?vendor=0&keywords=455-1719-ND
0473460001 (Molex) | CONN RCPT 5POS MICRO USB R/A | J5(USB) | 1 | http://www.digikey.com/product-detail/en/0473460001/WM17141CT-ND/1782474
FTMH-102-03-L-DV | CONN HEADER 4POS DUAL 1MM SMD | J6, J7 | 1 | http://www.digikey.com/product-detail/en/FTMH-102-03-L-DV/SAM1131-02-ND/1104451
SML-512UWT86 | LED 630NM RED WATER CLR 0603 SMD | D1, D4 | 2 | http://www.digikey.com/product-detail/en/SML-512UWT86/511-1314-1-ND/637127
SML-512MWT86 | LED 570NM GRN WHT/DIFF 0603 SMD | D2, D6 | 2 | http://www.digikey.com/product-detail/en/SML-512MWT86/511-1313-1-ND/637126
SML-512WWT86 | LED 590NM YLW WATER CLR 0603 SMD | D3,D7 | 2 | http://www.digikey.com/product-detail/en/SML-512WWT86/511-1315-1-ND/637128
SML512BC4TT86 | LED 468NM BLUE TRANSPARENT 1608 | D5 | 1 | http://www.digikey.com/product-search/en?vendor=0&keywords=SML512BC4TT86
B3U-3000P | SWITCH TACTILE SPST-NO 0.05A 12V | S1, S2 | 2 | http://www.digikey.com/product-detail/en/B3U-3000P/SW1022CT-ND/1534359
Capacitor
1pF(0402) | CAP CER 1PF 50V C0H 0402 | C38 | 1 | http://www.digikey.com/product-detail/en/UVK105CH010BW-F/587-1007-1-ND/930784
12pF | CAP CER 12PF 50V 5% C0G 0603 | C10, C11 | 2 | http://www.digikey.com/product-detail/en/C1608C0G1H120J080AA/445-1270-1-ND/567672
22pF | CAP CER 22PF 50V 5% C0G 0603 | C8, C9, C44 | 3 | http://www.digikey.com/product-detail/en/C1608C0G1H220J080AA/445-1273-1-ND/567670
47pF | CAP CER 47PF 50V 2% C0G 0402 | C23, C24 | 2 | http://www.digikey.com/product-detail/en/C1608C0G1H470J080AA/445-1277-1-ND/567679
2.2nF | CAP CER 2200PF 50V 5% C0G 0603 | C6, C33 | 2 | http://www.digikey.com/product-detail/en/C1608C0G1H222J080AA/445-1297-1-ND/567684
10nF | CAP CER 10000PF 50V 10% X7R 0603 | C21, C25 | 2 | http://www.digikey.com/product-detail/en/C1608X7R1H103K080AA/445-1311-1-ND/567691
100nF | CAP CER 0.1UF 25V 10% X7R 0603 | C3, C4, C5, C17, C20, C32, C35, C37, C39, C40, C41, C42, | 12 | http://www.digikey.com/product-detail/en/C1608X7R1E104K080AA/445-1316-1-ND/567697
1uF | CAP CER 1UF 16V 10% X5R 0603 | C1, C2, C7, C18, C22, C36 | 6 | http://www.digikey.com/product-detail/en/C1608X5R1C105K080AA/445-1416-1-ND/569082
4.7uF | CAP CER 4.7UF 6.3V 10% X5R 0603 | C19 | 1 | http://www.digikey.com/product-detail/en/C1608X5R0J475K080AB/445-5178-1-ND/2093793
10uF | CAP CER 10UF 6.3V 20% X5R 0603 | C34 | 1 | http://www.digikey.com/product-detail/en/C1608X5R0J475M080AB/445-1417-1-ND/569083
Resistor
0 | RES SMD 0.0 OHM JUMPER 1/10W | R40 | 1 | http://www.digikey.com/product-detail/en/ERJ-3GEY0R00V/P0.0GCT-ND/134711
33 | RES 33 OHM 1/10W 1% 0603 SMD | R14, R15 | 2 | http://www.digikey.com/product-detail/en/MCR03ERTF33R0/RHM33.0CFCT-ND/2796481
2.2k | RES 2.2K OHM 1/10W 1% 0603 SMD | R5, R6, R8, R9, R10, R11, R27 | 7 | http://www.digikey.com/product-detail/en/RC0603FR-072K2L/311-2.20KHRCT-ND/729963
3k | RES 3K OHM 1/10W 1% 0603 SMD | R48, R49, R13 | 3 | http://www.digikey.com/product-detail/en/MCR03ERTF3001/RHM3.00KCFCT-ND/2796477
10k | RES 10K OHM 1/10W 5% 0603 SMD | R1, R2, R12 | 3 | http://www.digikey.com/product-detail/en/RC0603JR-0710KL/311-10KGRCT-ND/729647
47k | RES 47K OHM 1/10W 1% 0603 SMD | R4, R7, R19, R25, R26 | 5 | http://www.digikey.com/product-detail/en/RC0603FR-0747KL/311-47.0KHRCT-ND/730200
49.9k | RES 49.9K OHM 1/10W 1% 0603 SMD | R20, R21, R22, R23, R24 | 5 | http://www.digikey.com/product-detail/en/RMCF0603FT49K9/RMCF0603FT49K9CT-ND/1943101
56k | RES 56K OHM 1/10W 1% 0603 SMD | R3 | 1 | http://www.digikey.com/product-detail/en/RC0603FR-0756KL/311-56KHRCT-ND/2827943
1M | RES 1M OHM 1/10W 1% 0603 SMD | R17, R18 | 2 | http://www.digikey.com/product-detail/en/RC0603FR-071ML/311-1.00MHRCT-ND/729791
Inductor
3.9nH(0402) | CER INDUCTOR 3.9NH 0402 | L1 | 1 | http://www.digikey.com/product-detail/en/L-07C3N9SV6T/712-1459-1-ND/1915238
2.7nH(0402) | INDUCTOR 2.7NH 220MA 0402 | L2 | 1 | http://www.digikey.com/product-detail/en/LQP15MN2N7B02D/490-1129-1-ND/584575

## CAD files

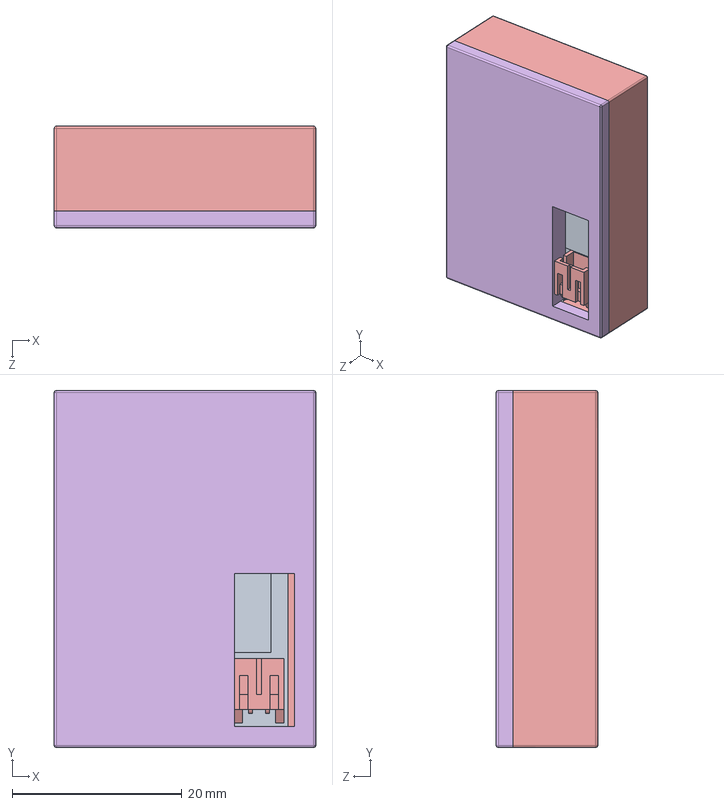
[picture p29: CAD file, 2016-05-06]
BenJohnston/MotionNet/Material Files/Solidworks Files/MotionNet3.SLDASM
30.9 x 42.1 x 12.0 mm
Board
B3U_3000P[] x 2
_FTMH-102-03-L-DV_body x 2
_FTMH-102-03-L-DV_pins1 x 2
S2B-PH-K-S
044-007-196_3M_2908-05WB-MG
Board_2
Extruded
Extruded_2
Extruded_3 x 2
Extruded_4
Enclosure Bottom
Enclosure Top

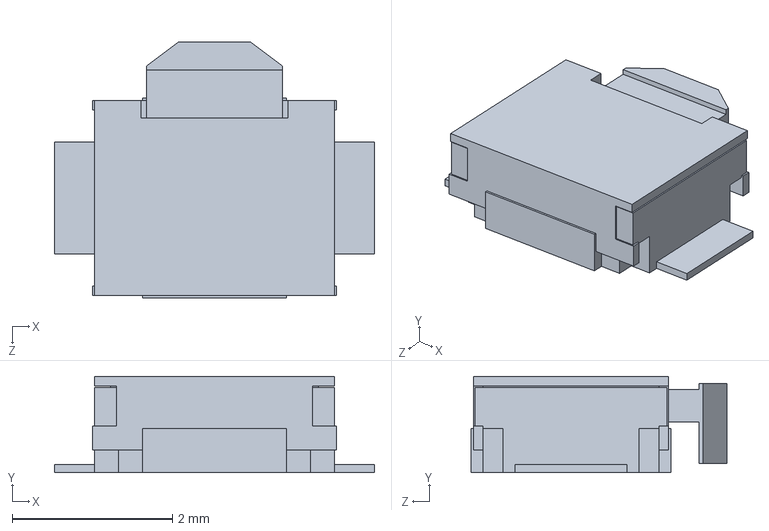
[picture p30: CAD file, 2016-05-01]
BenJohnston/MotionNet/Material Files/B3U_3000P[].step
4.00 x 1.20 x 3.20 mm

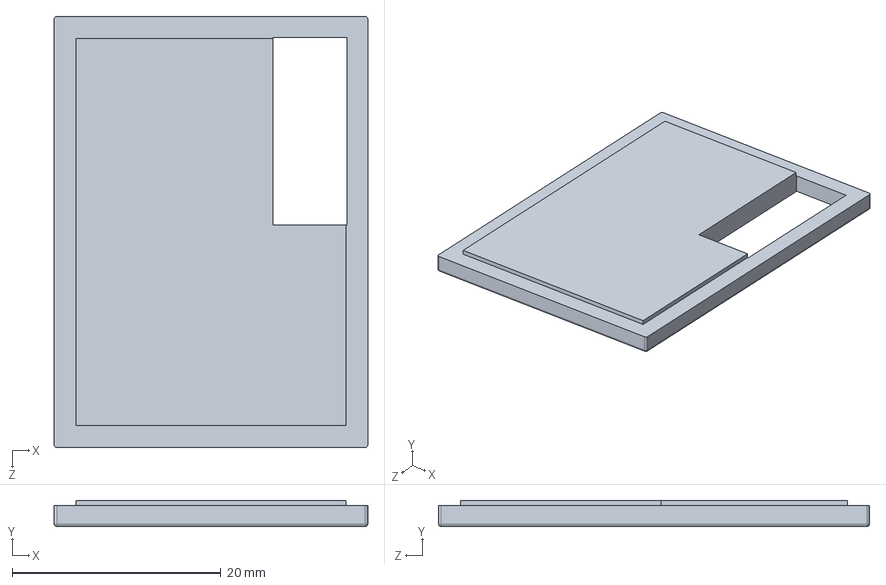
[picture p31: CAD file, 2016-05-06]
BenJohnston/MotionNet/Material Files/Solidworks Files/Enclosure Top.SLDPRT
30.1 x 2.50 x 41.3 mm

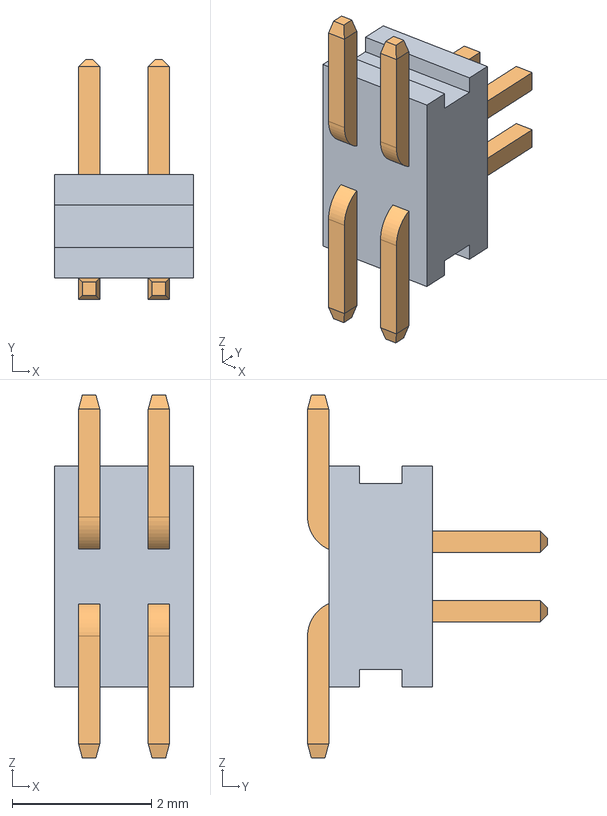
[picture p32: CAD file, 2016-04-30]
BenJohnston/MotionNet/Material Files/FTMH-102-03-L-DV.stp
2.00 x 3.44 x 5.21 mm
_FTMH-102-03-L-DV_body
_FTMH-102-03-L-DV_pins1

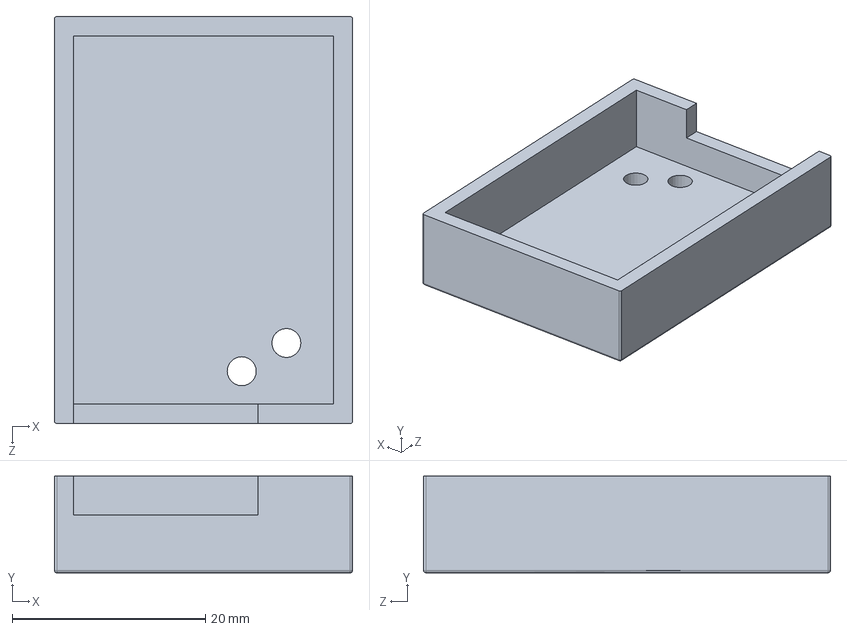
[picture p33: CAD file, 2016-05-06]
BenJohnston/MotionNet/Material Files/Solidworks Files/Enclosure Bottom.SLDPRT
30.9 x 10.0 x 42.1 mm

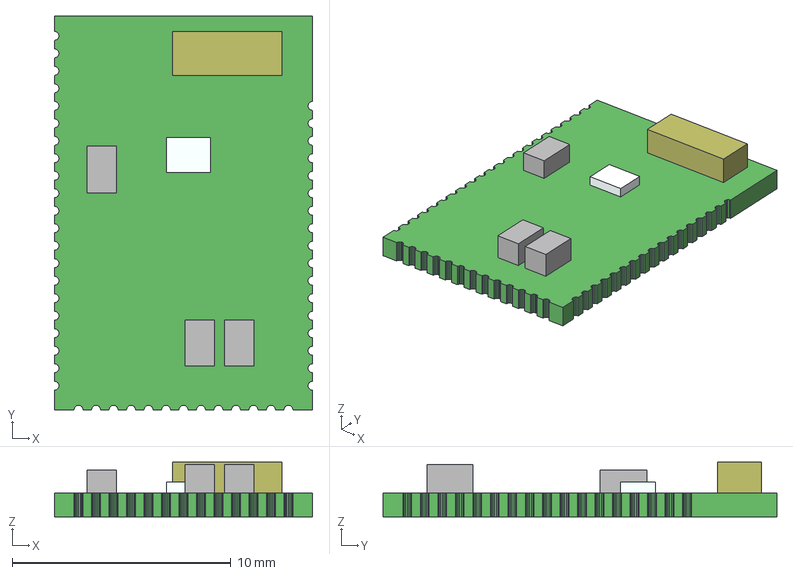
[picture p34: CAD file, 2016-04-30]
BenJohnston/MotionNet/Material Files/Blue Creation BC12x.step
11.8 x 18.0 x 2.50 mm
Board
Extruded x 5

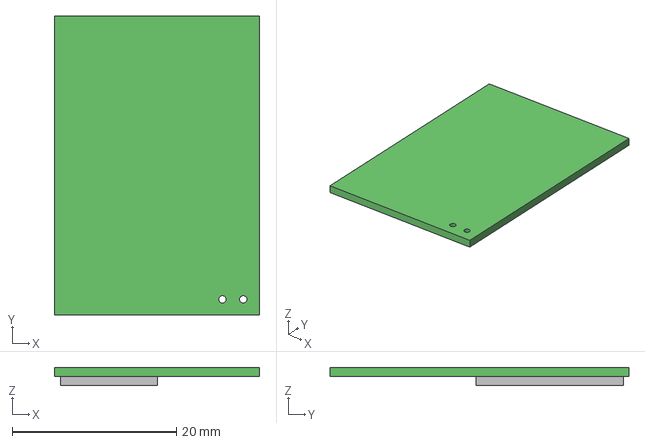
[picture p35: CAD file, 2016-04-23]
BenJohnston/MotionNet/Material Files/PCB1.step
25.0 x 36.4 x 2.23 mm
Board
Extruded

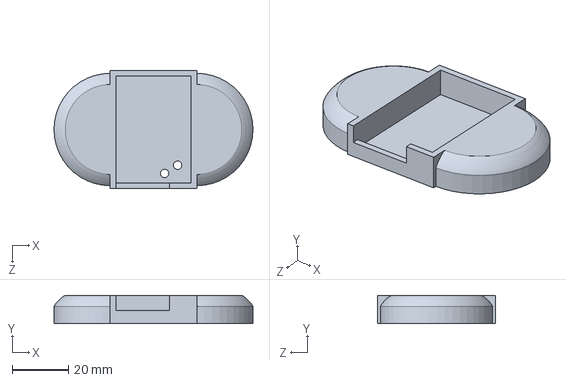
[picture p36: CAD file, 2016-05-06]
BenJohnston/MotionNet/Material Files/Solidworks Files/Enclosure Bottom Button.SLDPRT
70.9 x 10.0 x 42.1 mm

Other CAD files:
BenJohnston/MotionNet/Material Files/Solidworks Files/L2.sldasm
BenJohnston/MotionNet/Material Files/Solidworks Files/Free-Models.sldasm
BenJohnston/MotionNet/Material Files/Solidworks Files/X1.sldasm
BenJohnston/MotionNet/Material Files/Solidworks Files/L1.sldasm
BenJohnston/MotionNet/Material Files/Solidworks Files/ANT1.sldasm
BenJohnston/MotionNet/Material Files/Solidworks Files/F1.sldasm
BenJohnston/MotionNet/Material Files/Solidworks Files/Board.sldprt
BenJohnston/MotionNet/Material Files/Solidworks Files/_FTMH-102-03-L-DV_pins1.sldprt
BenJohnston/MotionNet/Material Files/Solidworks Files/Open CASCADE STEP translator 6.8 1.2.8.1.sldprt
BenJohnston/MotionNet/Material Files/473460001.stp
BenJohnston/MotionNet/Material Files/STL Files/Enclosure Bottom Button.STL
BenJohnston/MotionNet/Material Files/STL Files/Enclosure Bottom.STL
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

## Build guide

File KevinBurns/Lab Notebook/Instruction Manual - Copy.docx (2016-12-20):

Lower Back Disorder Quantification System Instruction Manual (Rev 1)

1. Run program
  a. OPTIONAL: Once program opens, press “Feedback Display” in order to open separate window to show real time patient position analysis for use in trial
2. Input window for COM port will appear. If COM port that IMU is connected to is known, enter value into window. If not:
  a. Press Start and navigate to Control Panel
3. Press initialize button once IMU COM port value is entered
  a. Program will set up connection to IMU(s)
4. Input relevant patient information into appropriate boxes (age, gender, etc)
5. OPTIONAL: Set directory for the collected data during trials to be stored in text files
6. Select a trial to capture:
  a. Trials 1-3: 0 degree flex exercise, see image below
  b. Trials 4-6: Rotate in transverse plane as far as is comfortable to the left of center and perform flex exercise, see image below
  c. Trials 7-9: Rotate in transverse plane as far as is comfortable to the right of center and perform flex exercise, see image below
  d. Trial 10: Repeatedly rotate back and forth to maximum comfortable regions in transverse plane, see image below
7. Once trial is selected, push “Start Trial” to being trial
  a. Patient will have 15 seconds to complete the exercise, or until the technician presses the manual stop button
8. Once trial is completed, press “Data Display”
  a. This will begin post processing of data, so a pause may be expected
  b. If all 10 trials have been completed when “Data Display” is selected, the quantification algorithm will complete and output the result
9. Select from the drop down menu which trial to plot and specify which data set is desired to be viewed, then press the “Graph” button to plot a visual representation of data

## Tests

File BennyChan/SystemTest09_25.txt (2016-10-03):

Lab Testing (9/25)
	Exercises
		No bending on knees
		Fast as possible but not hurt
		Hands on chest
		
1. Trial (10 exercises)
	1. 0 degree (15.71)
		1. T1
		2. Cal 1
	2. 0 degree (16.08)
		1. T2
		2. Cal 2
	3. 0 degree (15.51)
		1. T4 (T3 crashed)
		2. Cal 4 (Cal 3 crashed)
	4. 45 degrees left (15.46)
		1. T5
		2. Cal 5
	5. 45 degrees left (15.71)
		1. T6
		2. Cal 6
	6. 45 degrees left (15.49)
		1. T7
		2. Cal 7
	7. 45 degrees right (15.75)
		1. T8
		2. Cal 8
	8. 45 degrees right (15.74)
		1. T9
		2. Cal 9
	9. 45 degrees right (15.46)
		1. T10
		2. Cal 10
	10. sagittal twist (15.57)
		1. T11
		2. Cal 11

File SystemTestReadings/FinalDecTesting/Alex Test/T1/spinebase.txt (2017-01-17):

0.03386588 0.07495815 2.310174 Tracked 64272774
0.03394141 0.07476758 2.310003 Tracked 64272806
0.03394729 0.0747321 2.309957 Tracked 64272841
0.03393832 0.07471567 2.309951 Tracked 64272874
0.03399399 0.07461786 2.309896 Tracked 64272906
0.03404758 0.0746576 2.309851 Tracked 64272940
0.03404846 0.07467115 2.309868 Tracked 64272974
0.03413481 0.07474678 2.309965 Tracked 64273006
0.0345885 0.07541036 2.311 Tracked 64273041
0.03484661 0.07562551 2.312606 Tracked 64273073
0.03542763 0.07636292 2.31578 Tracked 64273106
0.03611778 0.07783297 2.321482 Tracked 64273140
0.03623743 0.07949626 2.326835 Tracked 64273173
0.03566185 0.08144903 2.334274 Tracked 64273206
0.03503285 0.08275682 2.343761 Tracked 64273241
0.03442229 0.08426518 2.352589 Tracked 64273275
0.03395033 0.08481503 2.3646 Tracked 64273314
0.03242878 0.08299869 2.377736 Tracked 64273341
0.03249626 0.07997976 2.392046 Tracked 64273374
0.03254306 0.07479969 2.407296 Tracked 64273406
0.03430332 0.1018792 2.492879 Tracked 64273441
0.03350487 0.09860996 2.496497 Tracked 64273474
0.03259887 0.09338073 2.514653 Tracked 64273507
0.03234989 0.08098613 2.524702 Tracked 64273540
0.03319446 0.08277356 2.544827 Tracked 64273573
0.033904 0.08283884 2.557786 Tracked 64273606
0.03219643 0.0813759 2.575503 Tracked 64273640
0.03314013 0.07569882 2.588035 Tracked 64273674
0.03359458 0.03555437 2.604742 Tracked 64273707
0.02882065 0.03782155 2.599874 Tracked 64273740
0.03072122 -0.009290949 2.625143 Tracked 64273773
0.03107625 -0.01201132 2.623845 Tracked 64273806
0.03232083 0.005875015 2.638368 Tracked 64273840
0.03438849 0.009666938 2.646033 Tracked 64273873
0.04233726 -0.03145692 2.653687 Tracked 64273906
0.03611849 -0.02879276 2.654245 Tracked 64273940
0.02801846 -0.0499007 2.652084 Tracked 64273974
0.01603545 -0.190631 2.631744 Tracked 64274006
0.06270458 -0.2506619 2.520518 Tracked 64274041
0.05219811 -0.2706687 2.444588 Tracked 64274077
0.04085343 -0.1886839 2.518865 Tracked 64274111
-0.009029977 -0.1471116 2.536744 Tracked 64274141
-0.01755632 -0.1225848 2.548741 Tracked 64274173
-0.03531836 0.1647331 2.660733 Tracked 64274206
0.004037695 0.1246586 2.650599 Tracked 64274240
0.01510662 0.129343 2.641357 Tracked 64274273
0.02546973 0.06936233 2.599079 Tracked 64274314
0.02621608 0.06862818 2.595338 Tracked 64274340
0.02654763 0.07487782 2.58058 Tracked 64274374
0.02737065 0.07596406 2.551615 Tracked 64274406
0.02857472 0.07853766 2.536843 Tracked 64274440
0.03395132 0.04335094 2.441756 Tracked 64274474
0.03246338 0.04760298 2.434464 Tracked 64274506
0.03174466 0.05771313 2.418549 Tracked 64274541
0.03401764 0.06570165 2.40306 Tracked 64274573
0.03459433 0.0675822 2.393106 Tracked 64274606
0.03594511 0.07329493 2.377423 Tracked 64274640
0.03714508 0.07324441 2.368128 Tracked 64274672
0.03664595 0.07399786 2.358946 Tracked 64274706
0.036673 0.0763376 2.350506 Tracked 64274748
0.0381247 0.0764856 2.344535 Tracked 64274776
0.03897703 0.07637699 2.338856 Tracked 64274807
0.0399843 0.07557211 2.334166 Tracked 64274843
0.04030518 0.07362593 2.329266 Tracked 64274876
0.04070447 0.07290825 2.326702 Tracked 64274911
0.04076265 0.07246425 2.325137 Tracked 64274946
0.04058705 0.07212678 2.323508 Tracked 64274980
0.04055072 0.0720262 2.322899 Tracked 64275007
0.04061349 0.07201087 2.322814 Tracked 64275040
0.0404785 0.07221958 2.323043 Tracked 64275074
0.04057813 0.07316287 2.32437 Tracked 64275108
0.03995271 0.07539903 2.327705 Tracked 64275141
0.03916139 0.07846713 2.333426 Tracked 64275176
0.03804962 0.08082195 2.342496 Tracked 64275208
0.03703941 0.08483755 2.354832 Tracked 64275242
0.0364028 0.08589454 2.364562 Tracked 64275275
0.03528475 0.0865467 2.37989 Tracked 64275308
0.03362617 0.08414721 2.39408 Tracked 64275342
0.03383356 0.0811042 2.407668 Tracked 64275373
0.03370525 0.07261596 2.42798 Tracked 64275406
0.03337794 0.0626623 2.445971 Tracked 64275440
0.03044535 0.07407741 2.505308 Tracked 64275473
0.03158375 0.06855929 2.507802 Tracked 64275506
0.03346718 0.04592496 2.518497 Tracked 64275541
0.03497329 0.03623856 2.526839 Tracked 64275574
0.03546059 0.03399492 2.547807 Tracked 64275606
0.03382818 0.02475476 2.557512 Tracked 64275641
0.03276698 0.02135167 2.569385 Tracked 64275673
0.03323355 0.01350807 2.57696 Tracked 64275706
0.03229348 -0.01096464 2.587472 Tracked 64275741
0.03582929 -0.0198398 2.598239 Tracked 64275774
0.04226265 -0.05737985 2.609893 Tracked 64275806
0.03716226 -0.08292111 2.607538 Tracked 64275841
0.03762252 -0.1582093 2.61262 Tracked 64275873
0.05002081 -0.2065161 2.590566 Tracked 64275906
0.02943723 -0.03032696 2.650043 Tracked 64275941
0.04134148 -0.1569634 2.61666 Tracked 64275974
0.04063366 -0.04948423 2.630682 Tracked 64276006
0.0338631 -0.1092434 2.597954 Tracked 64276040
0.03517965 -0.1090405 2.594486 Tracked 64276073
0.03806613 -0.079175 2.578171 Tracked 64276106
0.05481005 0.006677192 2.596246 Tracked 64276141
0.04258535 0.0301123 2.585605 Tracked 64276173
0.04025029 0.03037069 2.575267 Tracked 64276206
0.03654759 0.03021833 2.553271 Tracked 64276241
0.03641994 0.007268921 2.483586 Tracked 64276274
0.03730296 0.01711242 2.475536 Tracked 64276306
0.03693233 0.03302477 2.461211 Tracked 64276340
0.0374857 0.04468252 2.447257 Tracked 64276374
0.03783582 0.05859678 2.428111 Tracked 64276406
0.03828681 0.06493046 2.414198 Tracked 64276440
0.03793981 0.07106804 2.398664 Tracked 64276474
0.0373555 0.07546537 2.38215 Tracked 64276505
0.03772936 0.07807595 2.365873 Tracked 64276541
0.03805296 0.07776348 2.351469 Tracked 64276574
0.03889977 0.07834144 2.342007 Tracked 64276606
0.03894055 0.07550959 2.331483 Tracked 64276640
0.03889485 0.07392098 2.324116 Tracked 64276673
0.03869054 0.07174549 2.31703 Tracked 64276707
0.03820178 0.06986726 2.310919 Tracked 64276740
0.03800869 0.06819499 2.306277 Tracked 64276773
0.03794347 0.06741288 2.30321 Tracked 64276806
0.03784284 0.06671394 2.300975 Tracked 64276840
0.03793126 0.06626546 2.299611 Tracked 64276873
0.03793836 0.06616735 2.299445 Tracked 64276906
0.03795837 0.06617875 2.299434 Tracked 64276941
0.03811738 0.06668866 2.300559 Tracked 64276973
0.03818132 0.06780388 2.304776 Tracked 64277006
0.03759162 0.07255328 2.315007 Tracked 64277040
0.03775582 0.07841799 2.327276 Tracked 64277073
0.03655985 0.08509704 2.34393 Tracked 64277106
0.03640805 0.08945538 2.359255 Tracked 64277141
0.03552424 0.09212723 2.378893 Tracked 64277173
0.03560381 0.09244001 2.398732 Tracked 64277206
0.03345293 0.09135561 2.415428 Tracked 64277240
0.03316972 0.07676685 2.439129 Tracked 64277273
0.03401893 0.07011879 2.451811 Tracked 64277306
0.03487853 0.04945017 2.471334 Tracked 64277340
0.03603965 0.03117855 2.486934 Tracked 64277381
0.03928294 0.02283808 2.518108 Tracked 64277407
0.03811731 0.02052101 2.540701 Tracked 64277440
0.03618754 0.0169739 2.557208 Tracked 64277473
0.02989949 0.009838467 2.576059 Tracked 64277506
0.02232969 0.003715602 2.591636 Tracked 64277540
0.02102641 -0.0113166 2.599561 Tracked 64277574
0.0284605 -0.02028768 2.61726 Tracked 64277606
0.03520139 -0.1042334 2.614062 Tracked 64277640
0.03188153 -0.05377828 2.639423 Tracked 64277673
0.03710648 -0.07722053 2.64465 Tracked 64277705
0.03432791 -0.07880113 2.649433 Tracked 64277740
0.03475211 -0.07648569 2.651282 Tracked 64277773
0.04061987 -0.08892689 2.650876 Tracked 64277806
0.04469719 -0.1481111 2.617548 Tracked 64277840
0.0394532 -0.1103944 2.62314 Tracked 64277873
0.03959934 -0.1130118 2.620438 Tracked 64277906
0.005644195 -0.05838009 2.626222 Tracked 64277941
0.04214251 -0.006215544 2.615493 Tracked 64277974
0.03980681 0.01575919 2.610237 Tracked 64278005
0.03870795 0.02159077 2.602814 Tracked 64278040
0.036297 0.02659271 2.58096 Tracked 64278073
0.03692413 0.0004492489 2.50645 Tracked 64278106
0.03812243 0.01196676 2.500273 Tracked 64278140
0.03940241 0.02907151 2.487656 Tracked 64278173
0.03952162 0.04478766 2.471809 Tracked 64278206
0.03962695 0.05424381 2.456241 Tracked 64278240
0.03996688 0.06231663 2.439496 Tracked 64278273
0.04013117 0.06766634 2.423477 Tracked 64278306
0.04102791 0.06968444 2.405924 Tracked 64278340
0.04118609 0.07264036 2.389076 Tracked 64278381
0.04150275 0.07352764 2.378454 Tracked 64278411
0.04142809 0.07377156 2.36508 Tracked 64278446
0.04158032 0.07285991 2.351901 Tracked 64278481
0.04217544 0.07123692 2.3422 Tracked 64278512
0.04189966 0.07075615 2.335453 Tracked 64278547
0.04138991 0.06860708 2.327836 Tracked 64278574
0.04116173 0.06611934 2.3209 Tracked 64278607
0.04050427 0.06509117 2.316668 Tracked 64278641
0.04022907 0.0646819 2.314176 Tracked 64278675
0.0401978 0.06419234 2.311478 Tracked 64278709
0.04008541 0.06381516 2.310257 Tracked 64278743
0.03994226 0.06378124 2.310054 Tracked 64278776
0.03980023 0.0643143 2.310292 Tracked 64278809
0.03923287 0.06527364 2.311573 Tracked 64278843
0.03912745 0.06689344 2.314623 Tracked 64278876
0.03830467 0.07191557 2.322599 Tracked 64278909
0.03764046 0.0777394 2.333548 Tracked 64278943
0.03701043 0.08194852 2.346358 Tracked 64278976
0.0359869 0.08418382 2.362246 Tracked 64279010
0.03594838 0.08591332 2.379828 Tracked 64279043
0.03479991 0.08603694 2.400905 Tracked 64279074
0.03356703 0.08368742 2.418495 Tracked 64279106
0.03311242 0.07560922 2.44019 Tracked 64279140
0.03340867 0.06340043 2.460473 Tracked 64279174
0.03560353 0.07404743 2.52618 Tracked 64279205
0.03577795 0.06501129 2.530178 Tracked 64279240
0.0360727 0.04308084 2.547307 Tracked 64279274
0.03728212 0.03972633 2.565282 Tracked 64279306
0.03687024 0.04675485 2.5941 Tracked 64279340
0.03310125 0.04252815 2.607247 Tracked 64279373
0.03353734 0.03401433 2.618862 Tracked 64279406
0.01353977 -0.03923871 2.630695 Tracked 64279440
0.02586447 -0.08421178 2.6305 Tracked 64279474
0.02884567 -0.06550506 2.646337 Tracked 64279506
0.02867773 -0.07230408 2.649626 Tracked 64279540
0.03907393 0.005728662 2.66221 Tracked 64279573
0.03776954 -0.06407505 2.661511 Tracked 64279605
0.03749825 0.01224022 2.666566 Tracked 64279641
0.03193281 0.004726579 2.669487 Tracked 64279673
0.02449165 -0.05871441 2.672239 Tracked 64279707
0.02651741 -0.1524337 2.614964 Tracked 64279740
0.03190275 -0.1043604 2.618938 Tracked 64279773
0.02681975 -0.0908794 2.609311 Tracked 64279805
0.03354683 0.001761281 2.619421 Tracked 64279840
0.03194525 0.02268 2.61372 Tracked 64279873
0.03294999 0.02628548 2.60252 Tracked 64279906
0.03156929 0.03552977 2.586805 Tracked 64279940
0.03487583 0.01045418 2.503517 Tracked 64279973
0.03582626 0.01839904 2.497776 Tracked 64280006
0.03653515 0.03395775 2.48266 Tracked 64280040
0.03681817 0.04515305 2.465951 Tracked 64280073
0.03648592 0.05486262 2.450515 Tracked 64280107
0.03705906 0.06392574 2.432066 Tracked 64280140
0.03773624 0.06713258 2.419403 Tracked 64280173
0.03926488 0.0761973 2.398029 Tracked 64280205
0.03876361 0.07702246 2.386892 Tracked 64280241
0.03910232 0.07812523 2.374373 Tracked 64280273
0.03899014 0.07720907 2.365371 Tracked 64280306
0.03878766 0.07594563 2.356513 Tracked 64280340
0.03892778 0.07461948 2.348604 Tracked 64280374
0.03864061 0.07334612 2.342875 Tracked 64280407
0.03847485 0.07163748 2.337721 Tracked 64280440
0.03845797 0.07027771 2.333778 Tracked 64280474
0.03842903 0.06937575 2.331001 Tracked 64280506
0.03801646 0.06838772 2.329212 Tracked 64280540
0.03757528 0.06787615 2.328077 Tracked 64280573
0.0373573 0.06761525 2.327521 Tracked 64280606
0.03706102 0.06728839 2.327324 Tracked 64280640
0.03657973 0.06761918 2.32789 Tracked 64280673
0.03618699 0.06912957 2.33015 Tracked 64280706
0.03534637 0.07211871 2.335513 Tracked 64280741
0.03410387 0.07733761 2.348246 Tracked 64280773
0.03351723 0.08040073 2.357166 Tracked 64280806
0.03365753 0.0839066 2.370144 Tracked 64280840
0.03254633 0.08678309 2.386391 Tracked 64280873
0.03193487 0.0874882 2.401505 Tracked 64280906
0.03178881 0.08694569 2.420865 Tracked 64280941
0.03116396 0.08018257 2.439908 Tracked 64280974
0.03061243 0.07004061 2.46004 Tracked 64281005
0.03134974 0.05508518 2.477888 Tracked 64281041
0.03120752 0.06051791 2.535976 Tracked 64281074
0.03158811 0.05158882 2.543578 Tracked 64281106
0.03226956 0.03307412 2.556833 Tracked 64281140
0.03099499 0.03935474 2.590988 Tracked 64281174
0.02846289 0.0395934 2.604925 Tracked 64281206
0.01583573 0.009471604 2.615054 Tracked 64281241
0.02396002 -0.05027689 2.623787 Tracked 64281273
0.0256657 -0.05570438 2.629864 Tracked 64281305
0.0304419 -0.06160645 2.643191 Tracked 64281340
0.04751119 -9.081553E-05 2.658496 Tracked 64281374
0.04105384 0.006090372 2.662798 Tracked 64281406
0.03366141 -0.06097297 2.657582 Tracked 64281440
0.03628664 -0.04026935 2.660831 Tracked 64281478
0.04068261 -0.04603324 2.668431 Tracked 64281509
0.04028714 -0.04661953 2.668841 Tracked 64281543
0.02609688 -0.1355869 2.622643 Tracked 64281576
0.05026386 -0.06283713 2.643608 Tracked 64281608
-0.01053527 -0.05695944 2.614971 Tracked 64281642
0.04521694 -0.04914532 2.599334 Tracked 64281676
0.05084565 -0.0357151 2.585706 Tracked 64281709
0.04167761 -0.03394507 2.538503 Tracked 64281741
0.03183506 0.04494637 2.571316 Tracked 64281773
0.03499613 0.01641187 2.499743 Tracked 64281806
0.0358 0.02544174 2.492928 Tracked 64281840
0.03667877 0.0415525 2.47441 Tracked 64281873
0.03743307 0.05470623 2.458127 Tracked 64281906
0.03619015 0.06047378 2.4435 Tracked 64281940
0.03537159 0.07414026 2.415136 Tracked 64281974
0.03629506 0.07768102 2.402995 Tracked 64282009
0.03568641 0.07855899 2.387103 Tracked 64282043
0.03616272 0.07866148 2.375862 Tracked 64282076
0.03637183 0.07684625 2.363712 Tracked 64282109
0.03667735 0.07445258 2.353805 Tracked 64282142
0.03705623 0.07166193 2.345474 Tracked 64282175
0.03746402 0.07040108 2.34103 Tracked 64282208
0.03709256 0.06875511 2.336824 Tracked 64282242
0.03700196 0.06717741 2.332373 Tracked 64282276
0.03685225 0.06701862 2.329813 Tracked 64282309
0.03668189 0.06668897 2.32888 Tracked 64282342
0.03654534 0.06639893 2.328182 Tracked 64282376
0.03655371 0.06644662 2.328208 Tracked 64282409
0.03671162 0.06687281 2.32875 Tracked 64282451
0.03621519 0.06856637 2.331138 Tracked 64282481
0.035257 0.07219487 2.337747 Tracked 64282514
0.03426347 0.0767967 2.348097 Tracked 64282549
0.03322307 0.07979339 2.356819 Tracked 64282582
0.03322582 0.08324817 2.372749 Tracked 64282608
0.03184498 0.08658686 2.389437 Tracked 64282641
0.03176903 0.08811212 2.405793 Tracked 64282675
0.03143072 0.08825348 2.419782 Tracked 64282708
0.03119467 0.07941189 2.444176 Tracked 64282743
0.03119854 0.06849848 2.460973 Tracked 64282776
0.03380306 0.05466115 2.479405 Tracked 64282809
0.03456426 0.05881382 2.537986 Tracked 64282841
0.03411546 0.05054897 2.543772 Tracked 64282876
0.03445946 0.03881137 2.559042 Tracked 64282908
0.03335151 0.04439795 2.585032 Tracked 64282940
0.0308506 0.04056391 2.597593 Tracked 64282974
0.02809841 0.0281529 2.607336 Tracked 64283006
0.02622788 -0.03072102 2.627446 Tracked 64283041
0.03605779 -0.02409148 2.638208 Tracked 64283073
0.04743851 -0.1319781 2.623696 Tracked 64283106
0.04877659 -0.1338771 2.623467 Tracked 64283141
0.04508331 -0.03645038 2.658801 Tracked 64283173
0.04377206 -0.03244162 2.659359 Tracked 64283206
0.04706791 -0.03775138 2.657216 Tracked 64283241
0.07863423 -0.01320017 2.640606 Tracked 64283273
0.06996176 -0.0266021 2.647156 Tracked 64283306
0.03430663 -0.1648215 2.65248 Tracked 64283340
0.03981178 -0.08669157 2.626844 Tracked 64283374
0.03841211 -0.08481105 2.626033 Tracked 64283405
0.0235299 -0.03593205 2.620666 Tracked 64283440
0.03472352 -0.03835673 2.599156 Tracked 64283477
0.03550592 -0.02392406 2.583838 Tracked 64283506
0.03476257 0.03277414 2.574846 Tracked 64283540
0.03371948 0.03898971 2.570987 Tracked 64283574
0.03228846 0.01661317 2.487884 Tracked 64283606
0.03194577 0.02309975 2.481477 Tracked 64283640
0.03221731 0.0348784 2.465881 Tracked 64283673
0.03112433 0.05271824 2.443058 Tracked 64283706
0.03117072 0.05979335 2.430166 Tracked 64283740
0.03116063 0.06873086 2.411297 Tracked 64283773
0.03110648 0.074177 2.395894 Tracked 64283805
0.03119857 0.07545375 2.379172 Tracked 64283840
0.03108124 0.07517346 2.366482 Tracked 64283873
0.03155604 0.07472057 2.354403 Tracked 64283906
0.03250533 0.07214683 2.345401 Tracked 64283940
0.03347124 0.07007159 2.338892 Tracked 64283974
0.03333187 0.06808329 2.332358 Tracked 64284005
0.03372058 0.0665262 2.326962 Tracked 64284040
0.03380981 0.06520731 2.323079 Tracked 64284074
0.03370737 0.06433778 2.32031 Tracked 64284106
0.03382884 0.06374639 2.318672 Tracked 64284140
0.03389553 0.06336171 2.317844 Tracked 64284173
0.03398563 0.06315348 2.317568 Tracked 64284205
0.03407383 0.06320116 2.317653 Tracked 64284240
0.03415372 0.06370242 2.318346 Tracked 64284273
0.0347755 0.06516906 2.322681 Tracked 64284305
0.03447591 0.06787197 2.330982 Tracked 64284340
0.03427967 0.07291599 2.341265 Tracked 64284374
0.03357036 0.07779652 2.352434 Tracked 64284406
0.03321814 0.08213913 2.36679 Tracked 64284447
0.03289421 0.08511195 2.381304 Tracked 64284477
0.03240849 0.0868706 2.395484 Tracked 64284514
0.03144752 0.08759582 2.414044 Tracked 64284547
0.02963382 0.08584212 2.427825 Tracked 64284580
0.02905666 0.07679303 2.451143 Tracked 64284612
0.0299318 0.06638915 2.466851 Tracked 64284648
0.02722935 0.08290675 2.537592 Tracked 64284679
0.02724928 0.07487352 2.540678 Tracked 64284707
0.02563058 0.06163802 2.558497 Tracked 64284741
0.02637703 0.04374246 2.569062 Tracked 64284775
0.0244063 0.04508021 2.591581 Tracked 64284807
0.02337726 0.04884039 2.607679 Tracked 64284841
0.02233226 0.04843472 2.618529 Tracked 64284875
0.02003039 -0.05134542 2.617014 Tracked 64284907
0.02442798 -0.1328449 2.610904 Tracked 64284941
0.03281979 -0.03725445 2.662421 Tracked 64284973
0.04015369 -0.0659878 2.664439 Tracked 64285007
0.03806018 -0.0530466 2.660533 Tracked 64285041
0.03043992 0.01756642 2.659334 Tracked 64285075
0.03492836 0.02260855 2.65841 Tracked 64285108
0.04094046 0.02150352 2.658772 Tracked 64285141
0.04256476 0.01430486 2.66238 Tracked 64285174
0.04415339 -0.1479622 2.656541 Tracked 64285206
-0.0005122625 -0.1419073 2.609523 Tracked 64285241
0.03461023 0.02538043 2.6465 Tracked 64285274
0.03164305 0.02120603 2.641578 Tracked 64285308
0.01751523 -0.06097751 2.574842 Tracked 64285341
0.01474261 -0.01870322 2.573915 Tracked 64285374
0.02642331 0.03614597 2.580766 Tracked 64285407
0.02608088 0.04272819 2.576686 Tracked 64285441
0.031882 0.01960381 2.49158 Tracked 64285479
0.03229848 0.02650374 2.485017 Tracked 64285505
0.03228832 0.03684251 2.470445 Tracked 64285540
0.03029588 0.0533552 2.443729 Tracked 64285574
0.03065474 0.05921207 2.432299 Tracked 64285605
0.03001299 0.06708153 2.41306 Tracked 64285641
0.03153699 0.07459109 2.396042 Tracked 64285673
0.03196773 0.07660189 2.380005 Tracked 64285706
0.03239349 0.07697462 2.368103 Tracked 64285740
0.03360176 0.0753017 2.356699 Tracked 64285773
0.03455482 0.07273773 2.345705 Tracked 64285805
0.03519767 0.06954221 2.338843 Tracked 64285840
0.03520171 0.0673722 2.334027 Tracked 64285873
0.03561642 0.06545597 2.33034 Tracked 64285906
0.03571517 0.06326152 2.326536 Tracked 64285947
0.03579142 0.06266118 2.325075 Tracked 64285980
0.03585441 0.06251077 2.324586 Tracked 64286008
0.03585859 0.06245979 2.324163 Tracked 64286042
0.03582668 0.06241317 2.324165 Tracked 64286075
0.03586321 0.06254263 2.324656 Tracked 64286108
0.03586454 0.06332429 2.326432 Tracked 64286141
0.03578464 0.06635498 2.332004 Tracked 64286174
0.03476661 0.07107411 2.339648 Tracked 64286208
0.03342933 0.07581986 2.351981 Tracked 64286242
0.03325712 0.08000483 2.366043 Tracked 64286274
0.03261518 0.0835939 2.38384 Tracked 64286308
0.03186615 0.08494291 2.401572 Tracked 64286341
0.03098374 0.08416305 2.418481 Tracked 64286376
0.03124675 0.08019497 2.436076 Tracked 64286408
0.03210457 0.06996832 2.456891 Tracked 64286441
0.03304666 0.05961857 2.47377 Tracked 64286476
0.03008564 0.07038701 2.539958 Tracked 64286511
0.03070215 0.06309743 2.545552 Tracked 64286541
0.03125149 0.05137191 2.566261 Tracked 64286573
0.03054315 0.04579609 2.586044 Tracked 64286607
0.02822061 0.05068491 2.608206 Tracked 64286642
0.02772995 0.04969664 2.619452 Tracked 64286675
0.02687954 0.02406213 2.64536 Tracked 64286708
0.03633803 -0.1267992 2.616714 Tracked 64286742
0.04579087 -0.06199598 2.661475 Tracked 64286776
0.05988729 0.03704445 2.67641 Tracked 64286808
0.05389997 0.03176388 2.682468 Tracked 64286841
0.05695025 -0.02508006 2.657372 Tracked 64286875
0.04756719 -0.07877322 2.654198 Tracked 64286908
0.05627555 -0.0705612 2.655319 Tracked 64286942
0.05808209 -0.04909878 2.661645 Tracked 64286975
0.06011529 -0.1604292 2.660196 Tracked 64287009
0.1356249 -0.3790488 2.456054 Tracked 64287040
0.1388133 -0.3552261 2.419624 Tracked 64287074
0.02790421 0.0154465 2.673765 Tracked 64287108
0.02927984 0.02067104 2.670036 Tracked 64287142
0.02759774 -0.0403927 2.609327 Tracked 64287179
0.03670054 0.03052456 2.611041 Tracked 64287214
0.03558788 0.03587668 2.601833 Tracked 64287249
0.03419733 0.04386218 2.582268 Tracked 64287276
0.0333905 0.05471793 2.558493 Tracked 64287309
0.03714401 0.03428997 2.475838 Tracked 64287343
0.03704816 0.03963559 2.468451 Tracked 64287376
0.03743802 0.05539724 2.447401 Tracked 64287409
0.03699507 0.06086909 2.431972 Tracked 64287443
0.03505479 0.07136125 2.412512 Tracked 64287473
0.03550553 0.07605921 2.397503 Tracked 64287508
0.03491202 0.0783357 2.385786 Tracked 64287543
0.03452949 0.0792115 2.373041 Tracked 64287576
0.03456896 0.0779078 2.364714 Tracked 64287609
0.03463485 0.07645194 2.356002 Tracked 64287643
0.03495741 0.07474667 2.350917 Tracked 64287676
0.03514832 0.07377783 2.347195 Tracked 64287709
0.03517013 0.07301826 2.344409 Tracked 64287744
0.03515052 0.07232384 2.342775 Tracked 64287775
0.03514231 0.07211161 2.342199 Tracked 64287809
0.03508121 0.07220495 2.341995 Tracked 64287843
0.03498042 0.07243346 2.342062 Tracked 64287874
0.03456468 0.07324562 2.34321 Tracked 64287906
0.03378523 0.07588804 2.345972 Tracked 64287940
0.03325002 0.07782638 2.350449 Tracked 64287974
0.03351511 0.08091774 2.361725 Tracked 64288006
0.03310351 0.08251768 2.371236 Tracked 64288041
0.0326661 0.08412166 2.382227 Tracked 64288074
0.03287003 0.08451882 2.398851 Tracked 64288106
0.03189002 0.08226197 2.415216 Tracked 64288140
0.03325284 0.07535473 2.434042 Tracked 64288173
0.03292123 0.06646648 2.453254 Tracked 64288206
0.03034534 0.08455696 2.52179 Tracked 64288241
0.02926972 0.07988957 2.527588 Tracked 64288273
0.02788144 0.06770272 2.544789 Tracked 64288306
0.02743516 0.06136409 2.560368 Tracked 64288341
0.02671282 0.06228458 2.58839 Tracked 64288374
0.026966 0.06984343 2.602952 Tracked 64288406
0.02530835 0.0684984 2.610012 Tracked 64288441
0.02324227 0.02445312 2.628361 Tracked 64288473
0.01902186 0.03016594 2.631134 Tracked 64288506
0.0363913 -0.07577998 2.621846 Tracked 64288546
0.03553347 -0.1485256 2.596797 Tracked 64288573
0.03179767 -0.1292792 2.609212 Tracked 64288606
0.03823746 -0.06646708 2.611873 Tracked 64288640
0.02080533 -0.1190876 2.573169 Tracked 64288677
0.01076285 0.02681657 2.621341 Tracked 64288715
0.01140609 -0.05016702 2.577106 Tracked 64288742

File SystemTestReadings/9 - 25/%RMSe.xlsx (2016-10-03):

Trial | % RMS error | Trial | Kinect Mean | Vicon Mean | Mean Diff
1 | 16.1693 | 1 | 53.7786 | 44.1744 | 9.6042
2 | 15.5316 | 2 | 56.6584 | 46.7118 | 9.9466
3 | 40.377 | 3 | 52.5263 | 44.8297 | 7.6966
4 | 39.9142 | 4 | 56.7593 | 44.7862 | 11.9731
5 | 15.5456 | 5 | 58.6343 | 46.1638 | 12.4705
6 | 16.4486 | 6 | 58.7251 | 47.2282 | 11.4969
7 | 21.2303 | 7 | 61.0196 | 48.7837 | 12.2359
8 | 17.6615 | 8 | 61.1412 | 49.8239 | 11.3173
9 | 38.3734 | 9 | 59.6146 | 48.0592 | 11.5554
10 | 8.8399 | 10 | 79.7464 | 86.8241 | 7.0777
Avg. | 23.00914 | Avg. | 59.86038 | 50.7385 | 9.12188

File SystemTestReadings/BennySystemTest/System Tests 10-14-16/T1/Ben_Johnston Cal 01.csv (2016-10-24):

Trajectories
100
 |  | Ben_Johnston:Base |  |  | Ben_Johnston:L5 |  |  | Ben_Johnston:UpperVert |  |  | Ben_Johnston:Shoulder
Frame | Sub Frame | X | Y | Z | X | Y | Z | X | Y | Z | X | Y | Z
 |  | mm | mm | mm | mm | mm | mm | mm | mm | mm | mm | mm | mm
1 | 0 | 34.5689 | 372.591 | 1020.5 | 37.3937 | 400 | 1196.72 | 45.2835 | 359.858 | 1461.92 | -64.0629 | 400.001 | 1352.22
2 | 0 | 34.6895 | 372.423 | 1020.48 | 37.4169 | 399.823 | 1196.73 | 45.3989 | 359.568 | 1461.95 | -63.9907 | 399.753 | 1352.24
3 | 0 | 34.7909 | 372.277 | 1020.46 | 37.4898 | 399.596 | 1196.77 | 45.4795 | 359.311 | 1461.99 | -63.8539 | 399.419 | 1352.28
4 | 0 | 34.8765 | 372.159 | 1020.45 | 37.5705 | 399.342 | 1196.86 | 45.6196 | 359.003 | 1462.03 | -63.7058 | 399.048 | 1352.37
5 | 0 | 34.958 | 372.082 | 1020.43 | 37.6433 | 399.078 | 1196.98 | 45.7882 | 358.655 | 1462.1 | -63.6135 | 398.702 | 1352.47
6 | 0 | 35.0324 | 372.008 | 1020.44 | 37.7267 | 398.858 | 1197.14 | 45.9293 | 358.244 | 1462.16 | -63.5224 | 398.351 | 1352.58
7 | 0 | 35.1417 | 371.97 | 1020.43 | 37.7721 | 398.602 | 1197.29 | 46.0618 | 357.821 | 1462.22 | -63.3808 | 397.874 | 1352.69
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

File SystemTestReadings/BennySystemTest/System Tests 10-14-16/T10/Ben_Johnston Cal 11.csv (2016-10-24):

Trajectories
100
 |  | Ben_Johnston:Base |  |  | Ben_Johnston:L5 |  |  | Ben_Johnston:UpperVert |  |  | Ben_Johnston:Shoulder
Frame | Sub Frame | X | Y | Z | X | Y | Z | X | Y | Z | X | Y | Z
 |  | mm | mm | mm | mm | mm | mm | mm | mm | mm | mm | mm | mm
1 | 0 | 40.5916 | 436.46 | 1022.15 | 47.3864 | 473.418 | 1214.3 | 40.6413 | 433.933 | 1459.97 | -60.665 | 478.013 | 1343.11
2 | 0 | 40.4829 | 436.674 | 1022.52 | 47.1125 | 473.341 | 1214.58 | 40.2878 | 433.688 | 1460.16 | -61.044 | 477.531 | 1343.26
3 | 0 | 40.3372 | 436.961 | 1022.89 | 46.6735 | 473.297 | 1214.88 | 39.866 | 433.423 | 1460.42 | -61.5832 | 476.971 | 1343.47
4 | 0 | 40.1028 | 437.405 | 1023.17 | 46.1383 | 473.375 | 1215.32 | 39.3037 | 433.094 | 1460.67 | -62.2161 | 476.231 | 1343.72
5 | 0 | 39.774 | 438.059 | 1023.42 | 45.458 | 473.459 | 1215.87 | 38.6971 | 432.735 | 1460.96 | -63 | 475.384 | 1344.05
6 | 0 | 39.4069 | 438.723 | 1023.6 | 44.6812 | 473.592 | 1216.36 | 37.9742 | 432.286 | 1461.27 | -63.9321 | 474.456 | 1344.43
7 | 0 | 38.9152 | 439.559 | 1023.77 | 43.7868 | 473.793 | 1216.88 | 37.1898 | 431.832 | 1461.58 | -65.0255 | 473.426 | 1344.77
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

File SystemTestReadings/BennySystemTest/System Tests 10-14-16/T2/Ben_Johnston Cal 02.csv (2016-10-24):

Trajectories
100
 |  | Ben_Johnston:Base |  |  | Ben_Johnston:L5 |  |  | Ben_Johnston:UpperVert |  |  | Ben_Johnston:Shoulder
Frame | Sub Frame | X | Y | Z | X | Y | Z | X | Y | Z | X | Y | Z
 |  | mm | mm | mm | mm | mm | mm | mm | mm | mm | mm | mm | mm
1 | 0 | 31.3848 | 395.261 | 1016.67 | 35.4227 | 421.909 | 1189.95 | 40.8054 | 374.596 | 1459.29 | -66.8585 | 421.026 | 1350.12
2 | 0 | 31.3558 | 395.258 | 1016.67 | 35.404 | 421.806 | 1190 | 40.8055 | 374.449 | 1459.34 | -66.8513 | 420.871 | 1350.17
3 | 0 | 31.3243 | 395.24 | 1016.7 | 35.3413 | 421.701 | 1190.07 | 40.7998 | 374.31 | 1459.39 | -66.8754 | 420.679 | 1350.22
4 | 0 | 31.2967 | 395.228 | 1016.72 | 35.2739 | 421.575 | 1190.15 | 40.8252 | 374.162 | 1459.42 | -66.9276 | 420.449 | 1350.32
5 | 0 | 31.2608 | 395.211 | 1016.73 | 35.1932 | 421.465 | 1190.24 | 40.815 | 373.949 | 1459.49 | -66.9331 | 420.181 | 1350.38
6 | 0 | 31.2116 | 395.246 | 1016.74 | 35.1297 | 421.29 | 1190.34 | 40.8612 | 373.752 | 1459.55 | -66.9858 | 419.945 | 1350.46
7 | 0 | 31.1785 | 395.284 | 1016.73 | 35.029 | 421.152 | 1190.48 | 40.8356 | 373.54 | 1459.63 | -67.0493 | 419.653 | 1350.56
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

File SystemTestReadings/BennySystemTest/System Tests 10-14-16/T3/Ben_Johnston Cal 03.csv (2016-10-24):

Trajectories
100
 |  | Ben_Johnston:Base |  |  | Ben_Johnston:L5 |  |  | Ben_Johnston:UpperVert |  |  | Ben_Johnston:Shoulder
Frame | Sub Frame | X | Y | Z | X | Y | Z | X | Y | Z | X | Y | Z
 |  | mm | mm | mm | mm | mm | mm | mm | mm | mm | mm | mm | mm
1 | 0 | 55.101 | 406.089 | 1019.08 | 51.1323 | 429.852 | 1189.05 | 54.4353 | 398.496 | 1459.24 | -52.4307 | 438.387 | 1346.99
2 | 0 | 55.1113 | 406.055 | 1019.07 | 51.0739 | 429.781 | 1189 | 54.4411 | 398.62 | 1459.15 | -52.4906 | 438.353 | 1346.91
3 | 0 | 55.1375 | 406.033 | 1019.06 | 51.0457 | 429.67 | 1188.96 | 54.4617 | 398.684 | 1459.07 | -52.5404 | 438.261 | 1346.83
4 | 0 | 55.2075 | 406.011 | 1019.06 | 51.0544 | 429.544 | 1188.93 | 54.4905 | 398.702 | 1459.01 | -52.5616 | 438.097 | 1346.8
5 | 0 | 55.2507 | 405.97 | 1019.09 | 51.0637 | 429.338 | 1188.92 | 54.5446 | 398.68 | 1458.96 | -52.5611 | 437.894 | 1346.76
6 | 0 | 55.2994 | 405.988 | 1019.12 | 51.076 | 429.153 | 1188.93 | 54.5995 | 398.605 | 1458.93 | -52.5316 | 437.663 | 1346.75
7 | 0 | 55.311 | 405.969 | 1019.18 | 51.0797 | 428.944 | 1188.98 | 54.6575 | 398.476 | 1458.94 | -52.5005 | 437.371 | 1346.77
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

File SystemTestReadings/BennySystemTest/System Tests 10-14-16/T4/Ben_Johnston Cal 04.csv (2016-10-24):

Trajectories
100
 |  | Ben_Johnston:Base |  |  | Ben_Johnston:L5 |  |  | Ben_Johnston:UpperVert |  |  | Ben_Johnston:Shoulder
Frame | Sub Frame | X | Y | Z | X | Y | Z | X | Y | Z | X | Y | Z
 |  | mm | mm | mm | mm | mm | mm | mm | mm | mm | mm | mm | mm
1 | 0 | -10.6915 | 357.945 | 1018.85 | -28.6438 | 382.122 | 1185.32 | -26.0374 | 353.459 | 1454.79 | -135.637 | 339.961 | 1340.41
2 | 0 | -10.9606 | 358.24 | 1018.9 | -28.4348 | 381.722 | 1185.65 | -25.1821 | 352.559 | 1454.99 | -134.834 | 338.723 | 1340.73
3 | 0 | -11.3229 | 358.669 | 1018.92 | -28.0696 | 381.214 | 1186.12 | -24.1205 | 351.462 | 1455.19 | -133.957 | 337.353 | 1341.08
4 | 0 | -11.683 | 359.194 | 1018.91 | -27.8309 | 380.885 | 1186.66 | -23.1859 | 350.44 | 1455.51 | -133.096 | 335.901 | 1341.51
5 | 0 | -12.0617 | 359.895 | 1018.95 | -27.4511 | 380.466 | 1187.27 | -22.2929 | 349.522 | 1455.95 | -132.145 | 334.239 | 1342.06
6 | 0 | -12.3379 | 360.561 | 1019.04 | -26.9026 | 379.875 | 1187.88 | -21.0978 | 348.27 | 1456.36 | -131.103 | 332.444 | 1342.61
7 | 0 | -12.6505 | 361.444 | 1019.23 | -26.227 | 379.324 | 1188.59 | -19.9876 | 346.872 | 1456.82 | -129.891 | 330.51 | 1343.18
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

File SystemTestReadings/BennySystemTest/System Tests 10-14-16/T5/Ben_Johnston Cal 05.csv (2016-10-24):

Trajectories
100
 |  | Ben_Johnston:Base |  |  | Ben_Johnston:L5 |  |  | Ben_Johnston:UpperVert |  |  | Ben_Johnston:Shoulder
Frame | Sub Frame | X | Y | Z | X | Y | Z | X | Y | Z | X | Y | Z
 |  | mm | mm | mm | mm | mm | mm | mm | mm | mm | mm | mm | mm
1 | 0 | 7.90389 | 366.34 | 1027.55 | -6.51365 | 371.315 | 1196.11 | 3.33969 | 330.892 | 1463.06 | -105.937 | 311.875 | 1351.86
2 | 0 | 7.71401 | 367.035 | 1027.77 | -5.73875 | 370.648 | 1197.02 | 5.29513 | 328.766 | 1463.67 | -104.402 | 310.044 | 1352.9
3 | 0 | 7.42164 | 367.872 | 1028.02 | -4.99741 | 370.122 | 1198.01 | 7.52832 | 326.343 | 1464.31 | -102.785 | 308.078 | 1354.01
4 | 0 | 7.09305 | 368.698 | 1028.28 | -4.22752 | 369.493 | 1199.05 | 9.92398 | 323.824 | 1465 | -100.914 | 306.018 | 1355.12
5 | 0 | 6.72236 | 369.657 | 1028.64 | -3.45863 | 368.982 | 1200.25 | 12.4915 | 321.17 | 1465.74 | -98.9695 | 303.746 | 1356.34
6 | 0 | 6.25986 | 370.674 | 1029.09 | -2.73988 | 368.444 | 1201.52 | 15.2799 | 318.238 | 1466.51 | -96.9268 | 301.432 | 1357.72
7 | 0 | 5.73499 | 371.806 | 1029.67 | -2.01335 | 367.867 | 1202.95 | 18.2157 | 315.073 | 1467.3 | -94.7284 | 298.933 | 1359.22
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

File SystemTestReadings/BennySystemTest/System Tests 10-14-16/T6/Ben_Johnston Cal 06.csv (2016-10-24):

Trajectories
100
 |  | Ben_Johnston:Base |  |  | Ben_Johnston:L5 |  |  | Ben_Johnston:UpperVert |  |  | Ben_Johnston:Shoulder
Frame | Sub Frame | X | Y | Z | X | Y | Z | X | Y | Z | X | Y | Z
 |  | mm | mm | mm | mm | mm | mm | mm | mm | mm | mm | mm | mm
1 | 0 | -20.457 | 372.961 | 1015.71 | -48.8586 | 398.146 | 1179.9 | -47.2155 | 365.259 | 1453.64 | -153.207 | 347.696 | 1337.96
2 | 0 | -20.417 | 372.92 | 1015.79 | -48.786 | 397.703 | 1180.03 | -47.0916 | 364.966 | 1453.67 | -153.108 | 347.35 | 1338.12
3 | 0 | -20.3367 | 372.873 | 1015.88 | -48.674 | 397.209 | 1180.2 | -46.8819 | 364.61 | 1453.76 | -152.92 | 346.871 | 1338.26
4 | 0 | -20.1987 | 372.842 | 1016.01 | -48.5457 | 396.616 | 1180.38 | -46.6389 | 364.309 | 1453.87 | -152.711 | 346.321 | 1338.43
5 | 0 | -20.0588 | 372.811 | 1016.14 | -48.4155 | 396.075 | 1180.56 | -45.4706 | 362.403 | 1453.63 | -152.547 | 345.83 | 1338.67
6 | 0 | -19.8727 | 372.814 | 1016.27 | -48.2573 | 395.552 | 1180.76 | -45.1027 | 361.941 | 1453.73 | -152.278 | 345.196 | 1338.86
7 | 0 | -19.7223 | 372.793 | 1016.43 | -48.0526 | 394.897 | 1180.94 | -44.7606 | 361.537 | 1453.81 | -152.026 | 344.596 | 1339.04
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

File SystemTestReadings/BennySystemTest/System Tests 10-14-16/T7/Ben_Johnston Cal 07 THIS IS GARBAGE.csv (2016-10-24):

Trajectories
100
 |  | Ben_Johnston:Base |  |  | Ben_Johnston:L5 |  |  | Ben_Johnston:UpperVert |  |  | Ben_Johnston:Shoulder
Frame | Sub Frame | X | Y | Z | X | Y | Z | X | Y | Z | X | Y | Z
 |  | mm | mm | mm | mm | mm | mm | mm | mm | mm | mm | mm | mm
1 | 0 | 63.7557 | 397.652 | 1021.92 | 79.9986 | 420.042 | 1182.69 | 88.8435 | 392.016 | 1456.39 | -8.2459 | 453.604 | 1343.87
2 | 0 | 64.1128 | 398.069 | 1022.18 | 80.162 | 419.897 | 1183.16 | 88.2904 | 391.323 | 1456.81 | -8.47549 | 453.344 | 1344.28
3 | 0 | 64.5873 | 398.496 | 1022.5 | 80.3663 | 419.742 | 1183.73 | 87.6895 | 390.559 | 1457.25 | -8.71478 | 453.063 | 1344.73
4 | 0 | 65.0981 | 398.934 | 1022.81 | 80.6102 | 419.575 | 1184.35 | 86.9397 | 389.728 | 1457.73 | -8.94673 | 452.819 | 1345.23
5 | 0 | 65.699 | 399.442 | 1023.13 | 80.8942 | 419.348 | 1185.03 | 86.1439 | 388.813 | 1458.24 | -9.17517 | 452.554 | 1345.72
6 | 0 | 66.3565 | 399.983 | 1023.45 | 81.2969 | 418.997 | 1185.66 | 85.2745 | 387.797 | 1458.79 | -9.40447 | 452.226 | 1346.2
7 | 0 | 67.0889 | 400.61 | 1023.79 | 81.6515 | 418.635 | 1186.28 | 84.2278 | 386.627 | 1459.35 | -9.63483 | 451.854 | 1346.61
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

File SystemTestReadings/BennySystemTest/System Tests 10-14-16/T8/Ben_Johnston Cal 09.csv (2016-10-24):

Trajectories
100
 |  | Ben_Johnston:Base |  |  | Ben_Johnston:L5 |  |  | Ben_Johnston:UpperVert |  |  | Ben_Johnston:Shoulder
Frame | Sub Frame | X | Y | Z | X | Y | Z | X | Y | Z | X | Y | Z
 |  | mm | mm | mm | mm | mm | mm | mm | mm | mm | mm | mm | mm
1 | 0 | 35.7522 | 418.126 | 1017.73 | 53.3475 | 459.058 | 1210.8 | 55.5523 | 422.84 | 1454.41 | -47.6468 | 477.965 | 1342.05
2 | 0 | 35.7961 | 418.161 | 1017.8 | 53.3057 | 458.734 | 1211 | 55.4787 | 422.487 | 1454.51 | -47.6739 | 477.591 | 1342.15
3 | 0 | 35.916 | 418.231 | 1017.88 | 53.3052 | 458.439 | 1211.18 | 55.4054 | 422.025 | 1454.63 | -47.7405 | 477.207 | 1342.28
4 | 0 | 35.9752 | 418.325 | 1018.01 | 53.2539 | 458.016 | 1211.48 | 55.2779 | 421.519 | 1454.77 | -47.8614 | 476.762 | 1342.46
5 | 0 | 36.101 | 418.447 | 1018.19 | 53.1686 | 457.556 | 1211.79 | 55.0763 | 420.962 | 1454.99 | -47.9188 | 476.124 | 1342.68
6 | 0 | 36.2346 | 418.628 | 1018.41 | 53.0949 | 457.06 | 1212.16 | 54.9206 | 420.284 | 1455.27 | -48.1089 | 475.522 | 1342.97
7 | 0 | 36.362 | 418.872 | 1018.71 | 53.0452 | 456.575 | 1212.62 | 54.6413 | 419.503 | 1455.61 | -48.3076 | 474.863 | 1343.31
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

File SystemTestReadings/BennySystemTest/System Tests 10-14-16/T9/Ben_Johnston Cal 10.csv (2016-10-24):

Trajectories
100
 |  | Ben_Johnston:Base |  |  | Ben_Johnston:L5 |  |  | Ben_Johnston:UpperVert |  |  | Ben_Johnston:Shoulder
Frame | Sub Frame | X | Y | Z | X | Y | Z | X | Y | Z | X | Y | Z
 |  | mm | mm | mm | mm | mm | mm | mm | mm | mm | mm | mm | mm
1 | 0 | 30.8838 | 390.172 | 1021.46 | 44.6761 | 420.856 | 1218.05 | 37.5829 | 367.302 | 1461.73 | -57.9195 | 435.016 | 1349.87
2 | 0 | 31.1923 | 390.062 | 1021.76 | 44.3617 | 420.147 | 1218.49 | 36.664 | 366.021 | 1462.09 | -58.5377 | 434.256 | 1350.27
3 | 0 | 31.5913 | 390.053 | 1022.11 | 44.1942 | 419.484 | 1219.13 | 35.6085 | 364.731 | 1462.49 | -59.0856 | 433.45 | 1350.63
4 | 0 | 32.1151 | 390.049 | 1022.46 | 44.0657 | 418.589 | 1219.91 | 34.5032 | 363.345 | 1462.92 | -59.6997 | 432.551 | 1351.05
5 | 0 | 32.7206 | 390.189 | 1022.84 | 44.1264 | 417.843 | 1220.6 | 33.3015 | 361.885 | 1463.41 | -60.3286 | 431.78 | 1351.48
6 | 0 | 33.4072 | 390.394 | 1023.29 | 44.0434 | 416.805 | 1221.39 | 31.9569 | 360.362 | 1463.93 | -60.8756 | 430.756 | 1351.79
7 | 0 | 34.1608 | 390.665 | 1023.74 | 44.1368 | 415.87 | 1222.13 | 30.5173 | 358.694 | 1464.49 | -61.4879 | 429.843 | 1352.09
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

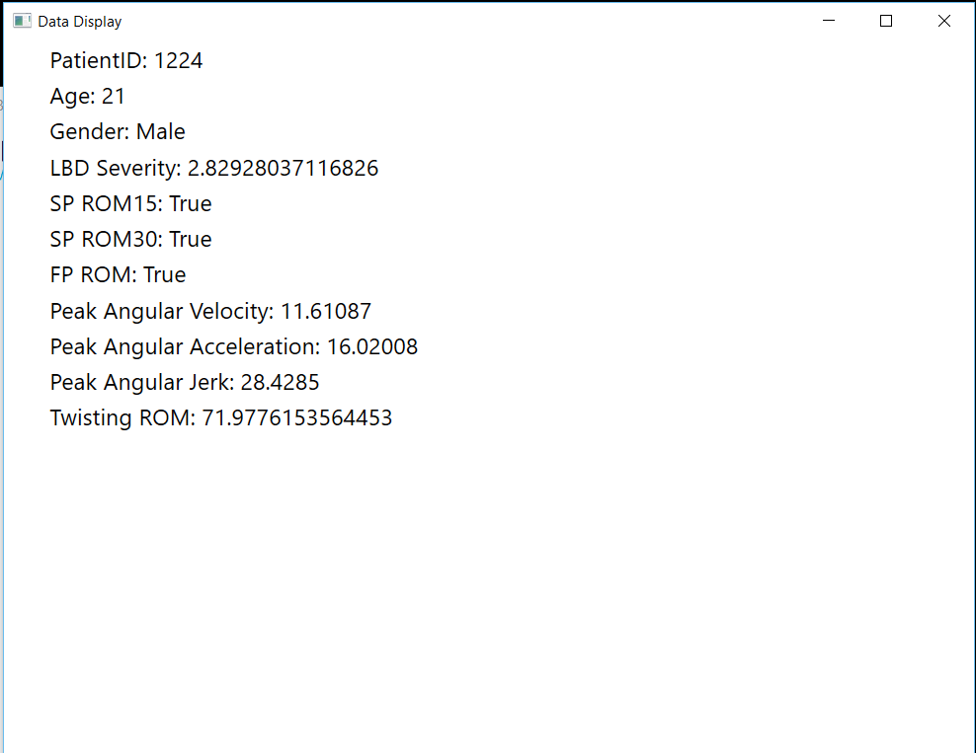
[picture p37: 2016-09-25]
AlexDubois/Good LBD Test.PNG

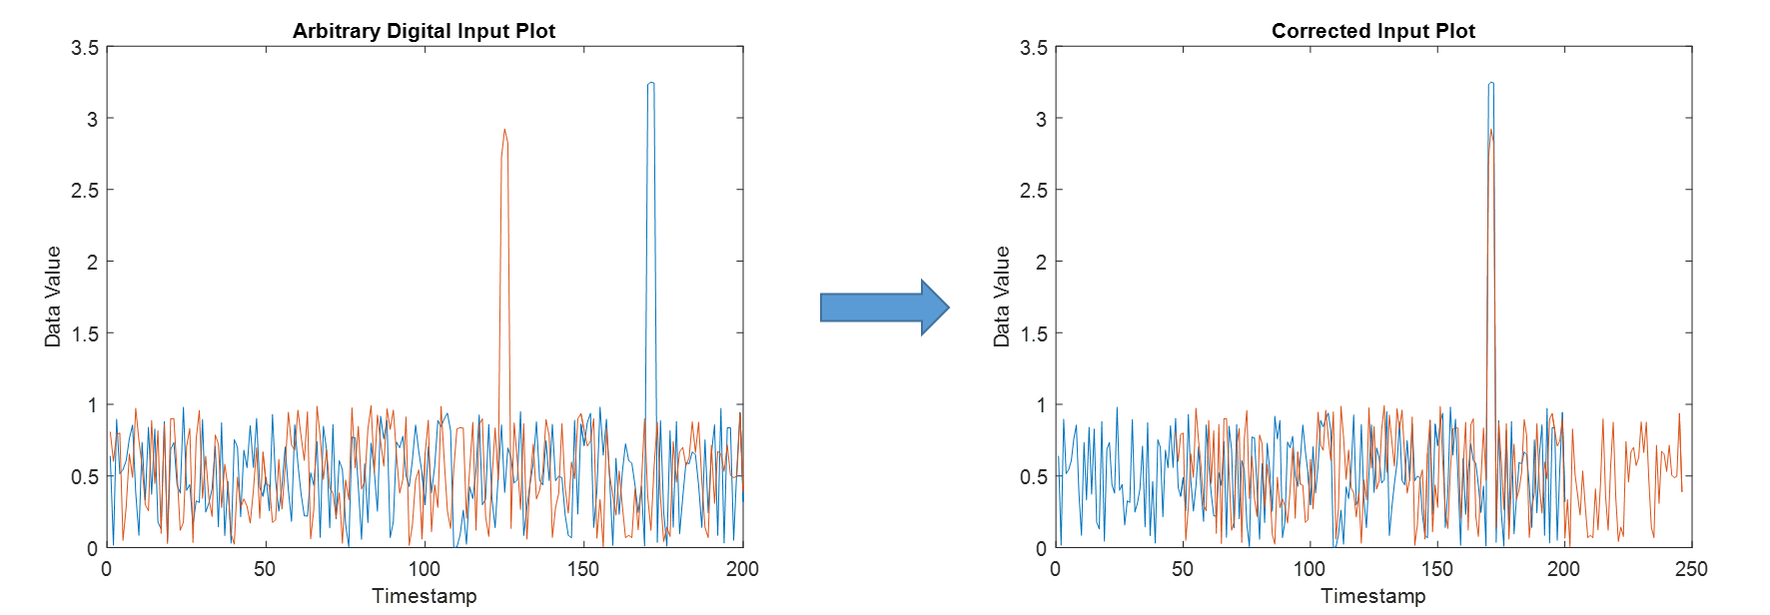
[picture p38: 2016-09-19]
KevinBurns/Charts, Graphs, and Images/Sync Result.png

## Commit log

2016-04-16 Updated Integrated Sensor Code and Added software flow charts for DDI and Data Analysis
2016-04-19 add quaternion libraries and MotionNet gerbers
    [PCB1.GBL, PCB1.GBO, PCB1.GBP, PCB1.GBS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]
2016-04-20 Created Database for DisplayFeedback, as well the GUI for the patient showing fundamental gestures for test. In addition, added realtime update of angle for the integrated sensors
2016-04-23 additional sensor testing
2016-04-25 'Added basic patient database'
2016-04-28 Add bill of materials
    [BOM.xlsx, PCB1.GBL, PCB1.GBO, PCB1.GBP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]
2016-04-30 PCB 3D model created, enclosure to come
    [473460001.stp, Blue Creation BC12x.step, FTMH-102-03-L-DV.stp, MotionNet.PcbDoc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]
2016-04-30 DDI shows basic info analyzed, quantification factor user input now included, and patient database now recieves all analyzed data
2016-04-30 Added end of semester software flowcharts
2016-04-30 Added end of semester software flowchart and kinect block diagram
2016-05-01 Enclosure First Draft
    [044-007-196_3M_2908-05WB-MG.sldprt, 473460001.sldasm, 485081456.sldasm, 485082224.sldasm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]
2016-05-01 Video Updates and STL Files
    [Enclosure Bottom.STL, Enclosure Top.STL]
2016-05-06 Next phase of enclosure design
    [Board.sldprt, Enclosure Bottom Button.SLDPRT, Enclosure Bottom Button.STL, Enclosure Bottom.SLDPRT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]
2016-09-19 Added Updated flowcharts for Kinect and Feedback Display
2016-09-19 Matlab Code Edits
    [Ben_Johnston Cal 01.csv, Ben_Johnston Cal 02.csv, Ben_Johnston Cal 03.csv, Ben_Johnston Cal 04.csv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]
2016-09-25 Updated LBD code, fixed IMU sensors in database, and added Vicon Test files
2016-09-26 Fixed flowcharts slightly
2016-09-26 Kin Filters, FiltFilt
    [Ben_Johnston Cal 03UP.csv]
2016-09-26 Bring system testing online, begin to rework code to use sensor fusion.
    [Ben_Johnston Cal 01.csv, Ben_Johnston Cal 02.csv, Ben_Johnston Cal 03.csv, Ben_Johnston Cal 04.csv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]
2016-09-26 Further sensor fusion work.
2016-09-26 Added matlab script to convert kinect spine mid and spine base data to flex angle
    [Ben_Johnston Cal 01.csv, Ben_Johnston Cal 02.csv, Ben_Johnston Cal 03.csv, Ben_Johnston Cal 04.csv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]
2016-10-01 Madgwick filter introduced
2016-10-03 Removed field for Patient ID which is now automatically calculated for easier testing and added matlab script for RMSE
2016-10-03 Added Timer for physician view
    [%RMSe.xlsx]
2016-10-20 Added test results and further polished results analysis scripts
    [Ben_Johnston Cal 01.csv, Ben_Johnston Cal 02.csv, Ben_Johnston Cal 03.csv, Ben_Johnston Cal 04.csv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]
2016-10-24 Add new files
    [Ben_Johnston Cal 01.csv, Ben_Johnston Cal 02.csv, Ben_Johnston Cal 03.csv, Ben_Johnston Cal 04.csv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]
2016-10-31 Updated VS project, and added updated flow charts and screenshots of flow charts
2016-11-27 Filtering implemented
2017-01-17 SystemTestReadings for December testing
    [Ben_Johnston Cal 01.csv, Ben_Johnston Cal 02.csv, Ben_Johnston Cal 05.csv, Ben_Johnston Cal 06.csv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]
